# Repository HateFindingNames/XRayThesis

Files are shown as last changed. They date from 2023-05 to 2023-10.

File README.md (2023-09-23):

<!-- LTeX: language=en-EN -->

- [1. :construction: Main Document](#1-construction-main-document)
- [2. 🔩 Hardware At Hand](#2--hardware-at-hand)
  - [2.1. Source](#21-source)
    - [2.1.1. 📜 Documentation](#211--documentation)
  - [2.2. Detector](#22-detector)
    - [2.2.1. 📜 Documentation](#221--documentation)
- [3. 👀 Stuff to do](#3--stuff-to-do)
- [4. 💸 Shopping Lists](#4--shopping-lists)
  - [4.1. Hardware](#41-hardware)
  - [4.2. Fasteners](#42-fasteners)
- [5. Drafting Area](#5-drafting-area)

# 1. :construction: Main Document

Since there is no reasonable way to track updated PDFs in git I will place them on [my Onedrive :globe_with_meridians:](https://hsrheinmain-my.sharepoint.com/:b:/g/personal/lmy9f42u92_hsrheinmain_onmicrosoft_com/EdXuY1hF2GhHoTZ-xGF3LT8B4NocIp0KUSrm5S4OvCQvuw?e=4TwyDO) until it is somewhat ready to publish.

# 2. 🔩 Hardware At Hand

## 2.1. Source

**Magpro TUB00154-SA-W06:**

* XRF and X-ray imaging
* 60kV (70 keV?)
* Spot size (.25 x 1.07)mm
* Cone divergence 48°
* ~17.6e3cps @ 16.4uA (40kV)

**SA** => SPI (**S**) and Analog (**A**) control type

**W06** => Tungsten target (transmition lines provided by [NIST](https://physics.nist.gov/cgi-bin/XrayTrans/search.pl?element=W&lower=&upper=&units=eV))

Made by [Moxtek](https://moxtek.com/) and distributed (EU) by [Quantum Design](https://qd-europe.com/de/de/)

### 2.1.1. 📜 Documentation

Available documentation can be found inside this repo:

* [DATASHEET_TUB00154-SA-W06.pdf](docs/OnPaper/DATASHEET_TUB00154-SA-W06/DATASHEET_TUB00154-SA-W06.pdf)
* [MANUAL_TUB-MAN-1007.pdf](docs/OnPaper/MANUAL_TUB-MAN-1007/MANUAL_TUB-MAN-1007.pdf)
* [TUB-DATA-1013-MAGPRO.pdf](docs/Online/TUB-DATA-1013-MAGPRO.pdf)

and on my OneDrive:

* [🔒 Moxtek MagPro 70kV  XRF Source (TUB00154-XX-XXX  TUB00155-XX-XXX) Product Specification (TUB-SPEC-1033) Rev H.pdf](https://hsrheinmain-my.sharepoint.com/:b:/g/personal/lmy9f42u92_hsrheinmain_onmicrosoft_com/EV1KUsbPE4NGpiN00cES0QcBQOVuTafLMZQphgjChVBe-A?email=daniel.muenstermann%40hs-rm.de&e=YY6j7k)
* [🔒 TUB00154-XX-XXX Mechanical Drawing.pdf](https://hsrheinmain-my.sharepoint.com/:b:/g/personal/lmy9f42u92_hsrheinmain_onmicrosoft_com/Eb5gZbNKkz1OtNJbWsKaR_sB0skO_YVYC2-HvIApNUwNWA?email=daniel.muenstermann%40hs-rm.de&e=mrExvE)

## 2.2. Detector

SDD Detector made by *PN Detector*: [XRS-A (All-in-One)](https://pndetector.de/products-applications/the-xrf-spectrometer-all-in-one/)
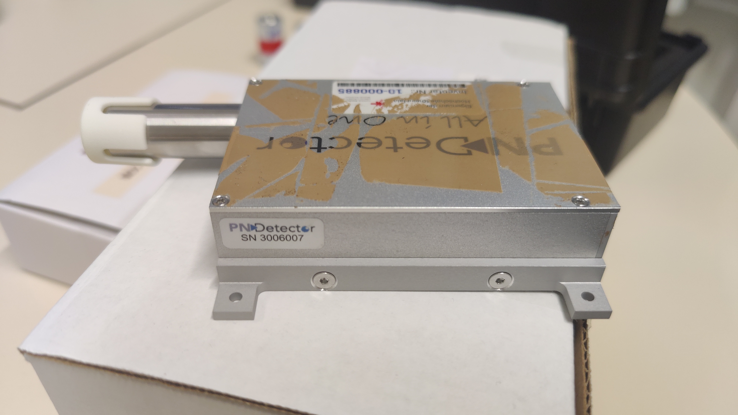
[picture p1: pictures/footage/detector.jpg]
SDD Detector


### 2.2.1. 📜 Documentation

OneDrive:

* [🔒 User Manual - XRS-A-30-128-200-MLC+GUI 0.1.1 -3006007.pdf](https://hsrheinmain-my.sharepoint.com/:b:/g/personal/lmy9f42u92_hsrheinmain_onmicrosoft_com/EWPr4Hw9F3tDvXxqMdxp95wBGIPgKuyxWKV6rSSlt5RyFA?email=daniel.muenstermann%40hs-rm.de&e=1WMr1p)

# 3. 👀 Stuff to do

In no particular order:

* [x] Text *[Quantum Design](https://qd-europe.com/de/de/)* about
  * [x] Linux-Software available?
  
    >*"No, only Microsoft"*

    * [ ] Make custom software?
  * [x] how to switch analog <=> digital control

    >*"10-pin is programmed for either I2C, SPI or Analog at the factory.  If a customer orders with Analog, they need to run digital through the USB or send back for reprograming and testing."*

  * [x] further documentation

    >*"FYI, 12W can operate down to -5kV setting, but the spec docs currently talk to the settings for 40kV and above.  If the customer wants to operate below 40kV, the voltage is scaled linearly from 0-4.667VDC for 0 to -70kV(but will not run at all at voltages less than -4kV setting), and 0-4VDC for 0 to 1000uA current setting.  Current needs to be limited to not exceed 12W total power, so 1,000uA does not work well above 12kV setting, and they will need to reduce the emission current as they select higher kV to keep power at or below 12W.  -W06 target is really not meant to be run below 40kV, as the W coating is thick enough that it blocks a majority of the flux intensity at kV settings below 30kV.  They can run down as low as 30kV, but stability may be affected in their application below 40kV setting."*

    Additional spec sheet and drawings are made available 👌 but are classified. => Plz check [OneDrive](https://hsrheinmain-my.sharepoint.com/:f:/g/personal/lmy9f42u92_hsrheinmain_onmicrosoft_com/Eu1u_OxAc6tNtfoioA8n_JEBt5x4kzV99mTDH0zqPgQLmQ?email=daniel.muenstermann%40hs-rm.de&e=uNh9up).
  * [x] CAD files => DIY
* [ ] Enclosure options
  * [ ] [Zarges-Boxes](https://www.zarges.com/de/produkte/verpacken-transportieren/kisten)?
  * [ ] [Rüger](https://www.rueger-industriebedarf.com/) (local distributer sells them among other, cheaper brands)
  * Interior modification:
    * [ ] Interlock
    * [ ] Pb-Shielding
      * [ ] Determine necessity
      * [ ] Find distributor => pre-order
* [ ] Make CAD-Model
* [x] Detector (check [*Amptek*](https://www.amptek.com/products/x-ray-detectors/x-ray-detector-selection-guide))
  * Options:
    * ~~**Si**licon **P**ositive **I**ntrinsic **N**egative Diode (Si-PIN Diode) (Wiki: [de](https://de.wikipedia.org/wiki/Pin-Diode),[en](https://en.wikipedia.org/wiki/PIN_diode))~~
    * 👉 **S**ilicone **D**rift **D**etector (SDD) (Wiki: [de](https://de.wikipedia.org/wiki/Siliziumdriftdetektor),[en](https://en.wikipedia.org/wiki/Silicon_drift_detector))
    * ~~**Ca**dmium **Te**lluride Schottky Diode (CdTe-Schottky)~~
* [ ] X-Ray optics

# 4. 💸 Shopping Lists

## 4.1. Hardware

| **Items**                                                                                                                                                                                                                                                              |        **Moneys** | **Vendors**           |    **Ordered**     |    **Arrived**     |
| ---------------------------------------------------------------------------------------------------------------------------------------------------------------------------------------------------------------------------------------------------------------------- | ----------------: | --------------------- | :----------------: | :----------------: |
| [Ball Bearing 635-2RS](https://www.kugellager-express.de/miniatur-kugellager-635-2rs-5x19x6-mm)                                                                                                                                                                        |        10 x 0.79€ | Kugellager-Express.de | :heavy_check_mark: | :heavy_check_mark: |
| [Ball Bearing 61708](https://www.kugellager-express.de/rillenkugellager-6708-61708-2rs-40x50x6-mm)                                                                                                                                                                     |         2 x 8.20€ | Kugellager-Express.de | :heavy_check_mark: | :heavy_check_mark: |
| [PRT-01-60](https://www.igus.de/product/iglidur_PRT_01_AL_J?artnr=PRT-01-60) (Slewing Bearing)                                                                                                                                                                         |           174.78€ | Igus.de               | :heavy_check_mark: | :heavy_check_mark: |
| Drag Chain                                                                                                                                                                                                                                                             | For free :muscle: | Igus.de               | :heavy_check_mark: | :heavy_check_mark: |
| ~~[Pulley 60T](https://www.amazon.de/Saipor-Zahnriemenrad-Riemenscheibe-Synchronrad-Zahnriemenscheibe/dp/B08ZSL7BH9/ref=sr_1_2?keywords=pulley%2B60t&sr=8-2&th=1)~~ printed                                                                                            |         ~~9.79€~~ | ~~Amazon.de~~         |        :x:         |                    |
| ~~[Pulley 20T](https://www.kris3d.de/products/pulley-20t-2gt-w9-b5-black)~~                                                                                                                                                                                            |     ~~2 x 3.99€~~ | ~~kris3d.de~~         |        :x:         |                    |
| [Belt 342-2MGT3-6](https://www.keilriemenexpress.de/zahnflachriemen-zahnriemen-shop/gates-zahnriemen-powergrip-gt3/zahnflachriemen-2m-gt3/zahnflachriemen-2m-gt3-6-mm/2mgt3-342-lw-6-mm-powergripr-gt3.html) (Sample)                                                  |            12.10€ | KeilriemenExpress.de  | :heavy_check_mark: |   :heavy_check_mark:                 |
| [Belt 600-2MGT3-9](https://www.keilriemenexpress.de/zahnflachriemen-zahnriemen-shop/gates-zahnriemen-powergrip-gt3/zahnflachriemen-2m-gt3/zahnflachriemen-2m-gt3-9-mm/2mgt3-600-lw-9-mm-powergripr-gt3.html) (Detector)                                                |            16.55€ | KeilriemenExpress.de  | :heavy_check_mark: | :heavy_check_mark: |
| [Filament eSun ASA 1kg](https://www.3djake.de/esun/easa-schwarz)                                                                                                                                                                                                       |        2 x 26.99€ | 3DJake.de             | :heavy_check_mark: | :heavy_check_mark: |
| ~~[Stepper Motors](https://www.amazon.de/STEPPERONLINE-Schrittmotor-55Ncm-Meter-3D-Drucker/dp/B0B93HTR87/ref=sr_1_6?__mk_de_DE=%C3%85M%C3%85%C5%BD%C3%95%C3%91&crid=2FD8SIDGO2PCX&keywords=stepperonline&sprefix=stepperonline%2Caps%2C98&sr=8-6&th=1)~~ self supplied |    ~~2 x 10.99€~~ | ~~Amazon.de~~         |        :x:         |                    |
| ~~[PSU 5V](https://www.digikey.de/en/products/detail/mean-well-usa-inc/RS-25-5/7706180)~~                                                                                                                                                                              |        ~~14.23€~~ | ~~Digikey.de~~        | :heavy_check_mark: | :heavy_check_mark:                   |
| ~~[PSU 24V](https://www.digikey.de/en/products/detail/mean-well-usa-inc/LRS-150-24/7705015)~~                                                                                                                                                                          |        ~~26.54€~~ | ~~Digikey.de~~        | :heavy_check_mark: | :heavy_check_mark:                   |
| [Aluminum Box](https://www.aluboxen-shop.de/aluboxen-mit-deckel/alukiste-xxl-130-liter)                                                                                                                                                                                |            99.90€ | aluboxen-shop.de      | :heavy_check_mark: |   :heavy_check_mark:                 |
| [Aluminum EN AW 5083 (8x505x770)mm](https://www.gemmel-metalle.de/aluminium/platten/5083/aluminiumplatte-213.html)                                                                                                                                                     |            96.70€ | gemmel-metalle.de     | :heavy_check_mark: |  :heavy_check_mark:                  |
| [Lead Sheet (1x300x5000)mm](https://sanundo.de/sonstiges/dach-zubehoer/walzblei/56046/selbstklebendes-farbiges-walzblei-bleicolor-sk-300mm-rotbraun-aehnlich-ral-8012-meterware)                                                                                       |            112.5€ | sanundo.de            |                    |                    |
| ~~Shipping (Alu, Lead)~~                                                                                                                                                                                                                                               |        ~~99.50€~~ | gemmel-metalle.de     |                    |                    |
| [Stepper Driver](https://www.digikey.de/de/products/detail/trinamic-motion-control-gmbh/TMC2209SILENTSTEPSTICK/10232488)                                                                                                                                               |        2 x 18.22€ | digikey.de            |                    |                    |
| ~~[DAC](https://www.digikey.de/de/products/detail/microchip-technology/MCP4912-E-P/2332828)~~ Self sourced    |             ~~2.86€~~ | digikey.de            |    :heavy_check_mark:                |      :heavy_check_mark:              |
| [ADC](https://de.rs-online.com/web/p/ad-wandler/0403115?gb=s)    |        2 x 4.68€ | rs-online.com.de            |     :heavy_check_mark:               |      :heavy_check_mark:              |
| [5V Reference](https://de.rs-online.com/web/p/referenzspannungs-ics/5343065?gb=s)    |        0.83€ | rs-online.com.de            |       :heavy_check_mark:             |       :heavy_check_mark:             |
| [2.5V Reference](https://de.rs-online.com/web/p/referenzspannungs-ics/5343059?gb=s)    |        0.92€ | rs-online.com.de            |          :heavy_check_mark:          |     :heavy_check_mark:               |
| ~~**Total**~~          |   ~~**637.73€**~~ |                       |        :x:         |                    |
| **Total**              |       **718.25€** |                       |        :x:         |                    |

## 4.2. Fasteners

| **Items**                                                                                                | **Moneys** | **Vendor**        |    **Ordered**     |    **Arrived**     |
| -------------------------------------------------------------------------------------------------------- | ---------: | ----------------- | :----------------: | :----------------: |
| [M5x25 DIN912](https://www.schraubenluchs.de/100-Stueck-Zylinderschrauben-ISO-4762-DIN-912-A2-70-M-5x25) |      5.75€ | schraubenluchs.de | :heavy_check_mark: | :heavy_check_mark: |
| [M5x50 DIN912](https://www.schraubenluchs.de/100-Stueck-Zylinderschrauben-ISO-4762-DIN-912-A2-70-M-5x50) |     14.65€ | schraubenluchs.de | :heavy_check_mark: | :heavy_check_mark: |
| [M5x20 DIN912](https://www.schraubenluchs.de/100-Stueck-Zylinderschrauben-ISO-4762-DIN-912-A2-70-M-5x20) |      4.82€ | schraubenluchs.de | :heavy_check_mark: | :heavy_check_mark: |
| [M5 Hex Nut](https://www.schraubenluchs.de/200-Stueck-Sechskantmuttern-DIN-934-A2-M5)                    |      2.50€ | schraubenluchs.de | :heavy_check_mark: | :heavy_check_mark: |
| **Total**                                                                                                | **27.72€** |                   |                    |                    |

# 5. Drafting Area

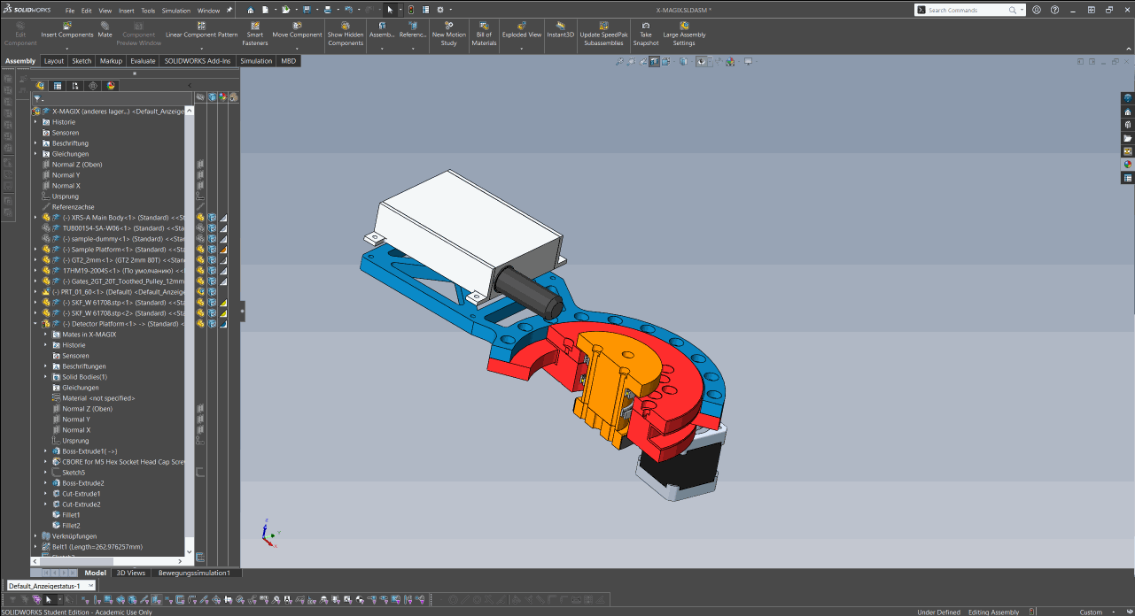
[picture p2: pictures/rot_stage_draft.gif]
Rotary stage WIP

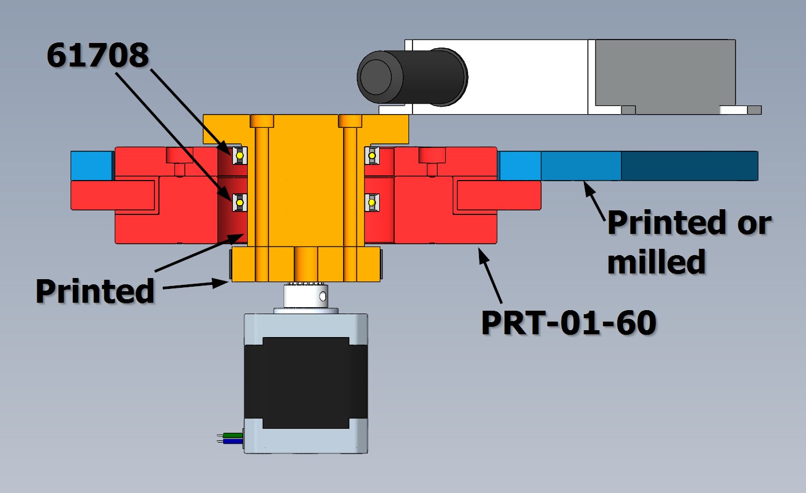
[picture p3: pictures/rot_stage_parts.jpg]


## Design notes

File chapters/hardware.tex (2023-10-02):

\chapter{Hardware}\label{chap:hardware}
    The hardware side consists of two mechanically connected but kinematically independent goniometer stages, static mounting components and an electrical part.
    The electronics are subdivided into the power supply, motion and logic handling and an interface between XRS/detector/motion system and the logic.

    \section{Mechanics}\label{sec:mechanics}
        Mechanically, the main challenge is to build two co-axial and co-planar but kinematically independent operating goniometer stages;
        One to move the detector and one to move the specimen about their mutual center of rotation as shown in~\cref{fig:rough sketch of the motion system}.
        \begin{figure}[!h]
            \centering
            \includesvg[width=.4\textwidth]{drawings/sketch_stages}%
            \caption[Rough sketch of the motion system]{Rough sketch of the motion system.}%
            \label{fig:rough sketch of the motion system}%
        \end{figure}
        Let the light bulb depicted in~\cref{fig:rough sketch of the motion system} be an x-ray source.
        The eye represents the detector and the specimen to analyze is positioned in the center\footnote{Clearly, an X-Ray source most likely will not be found in the fashion of an actual incandescent light bulb. Here, it merely serves as a visual shortcut representing a photon source. Furthermore, an actual eye performs rather poor at detecting \(\gamma\)-radiation. Thus, it, as well, shall serve the purpose of representation.}.
        The central stage carrying the sample varies the angle~\(\theta\), which is the angle enclosed by the incident beam path and the plane of the specimen.
        The detector stage~--~the outer circle in~\cref{fig:rough sketch of the motion system}~--~gets positioned along an angle~\(\varphi\).\par\medskip

        Since x-ray diffraction spectroscopy relies on angle-dependent intensity measurements both stages need to be capable of accurate and repeatable positioning at best possible angular resolution.
        Additionally, the detector stage needs to accelerate and carry the mass of the actual detector and its supporting structure.

        The rise of desktop 3D-printing and the growing communities around highly sophisticated open source/hardware machines has made components for high precision yet low cost motion systems in the low to lower-mid power range more available than ever.
        To this end, common 3D-printer parts are used where applicable.
        To achieve accuracy, a gearing system utilizing stepper motors, purpose-made timing pulleys and timing belts with a GT3 profile and~\qty{2}{\milli\metre} pitch are chosen~\cite{Manual.POWERGRIPGT3,Manual.LIGHTPOWERPRECISION}.
        
        To achieve and maintain repeatability~--~besides other factors~--~springiness in the motion system needs to be reduced to a minimum and slip during changes of torque e.g. direction changes and/or acceleration and deceleration needs to be eliminated.
        The former can reasonably easy be achieved by choosing fiberglass lined timing belts and proper preloading of the drive system removes residual slip.\par\medskip

        % A detailed description of the in this work proposed solutions are discussed in~\cref{sec:sample stage,,sec:detector stage}.
        
        \subsection{Sample Stage}\label{sec:sample stage}
            \Cref{fig:xmagix full sample highlightes} shows the main kinematic assembly and the sample stage with drive highlighted in light blue.
            \begin{figure}[!ht]
                \centering
                \includesvg[width=.7\textwidth]{drawings/X-MAGIX_full_sample}%
                \caption[Full motion system. Sample stage highlighted in light blue]{Full motion system. Sample stage highlighted in light blue.}%
                \label{fig:xmagix full sample highlightes}%
            \end{figure}%

            The center part of the main assembly is the slewing ring \textit{PRT-01-60} by \textsc{igus}~\cite{Manual.IglidePRTPolymerSlewingRings.} depicted as no. 24 in the section view in~\cref{fig:sample stage exploded section}.
            Its relatively large central hole gives room to place a smaller bearing assembly so that its is coaxial to its own axis of rotation.\par\medskip

            \begin{figure}[!h]
                \centering
                \includesvg[width=.3\textwidth]{pictures/footage/stage_bearings}
                \caption[Detailed photo of the stator center]{Detailed photo of the stator center. Close-up view of the press-in-place stator center locks (1). At the top and bottom are the \textit{W 61708} bearings visible (2) with the \textit{stator center spacer} in between (4). The outer part is the \textit{stator center} itself (3). All parts except the bearings are 3D-printed in acrylonitrile butadiene styrene (ABS).}%
                \label{fig:detailed view of the stator center}
            \end{figure}
            \nomenclature[A]{ABS}{Acrylonitrile butadiene styrene}

            The stationary part of the slewing ring provides two circular patterns of tapped bores fitting 10 M5 fasteners each.
            The holes along the inner circle are free to use.
            \textit{Stator center} (no.~4) is inserted into the slewing ring and held in place by seven \textit{M5x10} bolts (no.~22).
            Hereafter and in that sequence, the \textit{stator center spacer} (no.~5) and ball bearing \textit{W 61708-2RS} gets inserted into the free space from the top.
            The ball bearing is secured by press-fitting six of the \textit{stator locks} into their respective slots\footnote{ ``Abusing'' an ordinary drill-press to~--~well~--~press them in place (turned off!) works perfect.}.
            The final sub-assembly is shown in~\cref{fig:detailed view of the stator center}.

            With slight force, the remaining bearing is slid in its appropriate position from the bottom against the \textit{stator center spacer} as well.
            Finally, the \textit{sample driven gear} (no.~2) and the \textit{endstop bump sample} (no.~17) are tightened together against the \textit{sample platform} (no.~1) which is placed into the bearings beforehand.
            In order to guide the timing belt later, two bearings stacks are screwed from the bottom into two adjacent tapped holes.\par\medskip

            Not shown in~\cref{fig:sample stage exploded section} is the driving sub-assembly for the sample stage.
            Since its assembly is considered straightforward and a more complex version is shown in~\cref{fig:detector drive exploded}, an assembled view is found in~\cref{fig:sample drive} for reference.

            \begin{figure}[!h]
                \centering
                \includesvg[width=.8\textwidth]{drawings/sample_stage_-_exploded_section}%
                \caption[Sample stage exploded view~-~sectioned]{Sample stage exploded view~-~sectioned. 1: Sample Platform, 2: Sample Driven Gear 80T, 3: W 61708, 4: Stator Center, 5: Stator Center Spacer, 9: M5 Hex nut, 10: M5x25, 13: Washer 5.3, 16: 635-2RS, 17: Endstop Bump Sample, 19: M5x55, 20: M5x50, 21: Stator Center Spacer Lock, 22: M5x10, 24: PRT-01-60.}%
                \label{fig:sample stage exploded section}%
            \end{figure}

        \subsection{Detector Stage}\label{sec:detector stage}
            The components comprising the detector stage are depicted in~\cref{fig:xmagix full detector highlightes}.
            Its principle of operation follows the same basic concept~--~a timing belt mechanically couples the driving sub-assembly on the right-hand side to the movable central platform.\par\medskip

            \begin{figure}[!ht]
                \centering
                \includesvg[width=.7\textwidth]{drawings/X-MAGIX_full_detector}%
                \caption[Full motion system. Detector stage blue highlighted]{Full motion system. Detector stage blue highlighted.}%
                \label{fig:xmagix full detector highlightes}%
            \end{figure}

            Again, the detector stage is subdivided into a driving sub-assembly as shown in~\cref{fig:detector drive exploded} and driven one shown in~\cref{fig:detector stage exploded} respectively.
            The driven portion of the detector stage only consists of two main parts mounted to the slewing ring;
            The \textit{detector platform} (no.~25) which is placed on the top at an arbitrary orientation and the \textit{detector driven gear} (no.~26) on the bottom of the slewing ring.
            \textit{M5x25} (no.~10) bolts and \textit{hex nuts} (9) are placed into all holes but the two where the \textit{endstop bump detector} (no.~29) is mounted.
            To accommodate the needed extra length here, \textit{M5x30} (no.~42) bolts are used instead.
            The \textit{endstop bump detector} itself is oriented such that its outermost mounting hole is aligned with the hole at the clockwise end of the detector arm.
            To lift the detector to a suitable height above the \textit{sample platform}, \textit{detector spacers} (no.~30) are placed underneath the \textit{XRS-A} (no.~23).\par\medskip

            \Cref{fig:detector drive exploded} shows an exploded view of the detector drive sub-assembly.
            The core component, a NEMA17 \num{200} steps per revolution stepper motor (no.~7), is placed on the inside of the housing (no.~27) and held in place by four \textit{M3x6} screws.
            Slotted screw holes allow easier installation of the timing belt and adjustment of tension later on.
            Together with a \textit{hex nut} and the \textit{belt tensioner} (no.~8), a \textit{M5x25} bolt allows to hold the motor in place while tensioning the belt prior to finally tightening the screws at the top.

            \begin{figure}[!h]
                \centering
                \includesvg[width=.8\textwidth]{drawings/detector_stage_-_exploded}%
                \caption[Detector stage -- exploded view]{Detector stage -- exploded view. 9: M5 Hex Nut, 10: M5x25, 23: XRS-A, 25: Detector Platform, 26: Detector Driven Gear 250T, 29: Endstop Bump Detector, 30: Detector Spacer, 31: M3x25, 42: M5x30.}%
                \label{fig:detector stage exploded}%
            \end{figure}
            
            Bearing stacks identical to those seen in~\cref{fig:sample stage exploded} are put in place to confine the belt path along a \qty{180}{\degree} loop around the \textit{80T} timing pulley (no.~28).
            Having as many teeth of the belt engage the pulley at any given time is preferred as it ensures good torque transmission without belt slipping at a lower overall belt tension and thus lower load on the motors.
            \begin{figure}[!h]
                \centering
                \includesvg[height=.4\textheight]{drawings/detector_drive_-_exploded}
                \caption[Detector stage drive~--~exploded view]{Detector stage drive~-~exploded view. 7: 17HM19-2004S, 8: Belt Tightener, 9: M5 Hex nut, 10, M5x25, 11: Washer 3.2, 12: M3x6, 13: Washer 5.3, 14: Motor Mount Socket, 16: 635-2RS, 27: Motor Mount Detector Drive, 28: GT3 \qty{2}{\milli\meter} 80T.}
                \label{fig:detector drive exploded}
            \end{figure}

        \subsection{Base and X-Ray Source}
            \begin{figure}[!ht]
                \centering
                \includesvg[width=.6\textwidth]{drawings/source_exploded}
                \caption[short]{title}%
                \label{fig:source exploded}
            \end{figure}

    \clearpage
    \section{Electronics}\label{sec:electronics}
        On the electronics side, several tasks need to be accomplished, the most basic of which is powering each of the system's components.
        The SBC is typically powered via its dedicated USB-C port, which in turn requires a \qty{5.1}{\volt} supply with a recommended current rating of \qty{3}{\ampere}~\cite{Manual.Documentation.RPF}.
        The detector's specifications state that it needs a \qty{5}{\volt} power supply and draws less than \qty{3}{\watt}, which translates to \(<\qty{0.6}{\ampere}\).
        Taken from the datasheet, the XRS is driven by an input voltage of \qty{24}{\volt} and an input current of \qty{1.1}{\ampere}~\cite{Manual.MAGPRODataSheet.QD}.
        The two stepper motors are each driven by \textit{TMC2209} stepper drivers which in turn accept a relatively broad range of \qtyrange{4.75}{29}{\volt}~\cite{Manual.TMC2209Datasheet} as supply voltages.
        The remaining peripherals such as the interface between the SBC and the XRS are directly driven from \qty{3.3}{\volt} and \qty{5}{\volt} provided by the Raspberry Pi's GPIO-Header.

        A tabulated summery of the supply power requirements can be found in~\cref{tab:power requirements}.\par\medskip
        \begin{table}[!h]
            \centering
            \caption[Electrical power requirements of the various installed components]{Electrical power requirements of the various installed components.}%
            \label{tab:power requirements}
            \begin{tabular}{@{}lSS@{}}
                \toprule
                Component&  {Voltage / \unit{\volt}}&    {Current / \unit{\ampere}}\\
                \midrule
                SBC&            5.1&    3.0\\
                Detector&       5.0&    0.6\\
                XRS&            24.0&   1.1\\
                Motor Driver&   24.0&   3.0\\
                \bottomrule
            \end{tabular}
        \end{table}

        Following the considerations above, a \qty{5}{\volt} \qty{25}{\watt} power supply unit (PSU) \nomenclature[A]{PSU}{Power Supply Unit} (\textit{RS-25-5}) and a \qty{24}{\volt} \qty{150}{\watt} PSU (\textit{LRS-150-24}) are installed.
        Each is able to deliver slightly more power than expected to be necessary, thus, leaving headroom for future extensibility and peaks in power demand.
        The single \qty{24}{\volt}-PSU supplying the stepper drivers and the XRS minimizes complexity and reduces costs.\par\medskip

        All wiring~--~where applicable~--~is routed through perforated cable ducting.

        \subsection{Kinematics}\label{sec:kinematics}
            In addition to the two stepper motors driving each stage, at least one endstop needs to be installed per axis.
            Despite inferior durability compared to optical or magnetic options, mechanical micro switch type endstops were chosen due to availability and simplicity by requiring no additional passive components.
            \begin{figure}[h]
                \centering
                
                \caption[Wiring of the used mechanical endstops]{Wiring of the used mechanical endstops. They are installed in normal closed (NC) configuration to detect faulty connections early on.}%
                \label{fig:endstop pic}
            \end{figure}

            \Cref{fig:endstop pic} shows an example of one of the actual endstops used.
            They are wired in normally closed (NC) configuration to prevent potential damage by driving the stages past their minimal position during the homing procedures in case of an accidental connection break.

            \begin{figure}[h]
                \centering
                \includesvg[width=.9\textwidth]{electronics/pdf/octopus}
                \caption[Top view drawing of the \textit{Octopus v1.0} PCB layout]{Top view drawing of the \textit{Octopus v1.0} PCB layout~\cite{Manual.BigTreeTechOctopus}. Highlighted are the power terminals (1), the used motor (2) and endstop (3) connectors and the USB type C plug (4). The motors and the main power supply share the same \qty{24}{\volt} supply and are tied together.}%
                \label{fig:octopus connections}
            \end{figure}

            Low-level processing of the endstop signaling and stepping pulse generation takes place on dedicated peripheral hardware connected to the SBC via USB.
            Usually found in 3D-printing appliances, an \textit{Octopus v1.0} is installed to accept motion instructions from and return endstop signals to the host system.
            \Cref{fig:octopus connections} depicts a top view diagram of the \textit{Octopus'} PCB\footnote{Printed Circuit Board\nomenclature[A]{PCB}{Printed Circuit Board}} layout and highlights the relevant connectors and terminals~\cite{Manual.BigTreeTechOctopus}.
            The power supply terminals located on the left hand side serve as power supply to the connected motor drivers, the board itself and an~--~if installed~--~heated print bed.
            In this design, the motors and the primary power supply of the board share the same voltage level of \qty{24}{\volt} (1).
            The two motors are connected to the first two 4-pin connectors at the top of horizontal row labeled \texttt{MOTOR0} and \texttt{MOTOR1}(2).
            There are four dedicated endstop connectors (3) located on the bottom right, each providing a ground connection and \qty{3.3}{\volt}\footnote{Depending on the respective jumper placement \qty{5}{\volt} can be chosen as well. See~\cite{Manual.BigTreeTechOctopus} for the exact jumper location.}.

            \begin{table}[h]
                \centering
                \caption[\textit{Octopus} pin assignment]{\textit{Octopus} pin assignment.}
                \label{tab:octopus pin assignments}
                \begin{tabular}{@{}lrr@{}}
                    \toprule
                    Function&   X-axis pin& Y-axis pin\\
                    \midrule
                    Step&       PF13&   PG0\\
                    Direction&  PF12&   PG1\\
                    Enable&     !PF14&  !PF15\\
                    Endstop&    \textasciicircum PG6&   \textasciicircum PG9\\
                    Driver UART& PC4&   PD11\\
                    \bottomrule
                \end{tabular}
            \end{table}

            The endstop switches are connected between ground and the input pin with the internal pull-up resistor enabled.
            The host system is connected to the board via USB type C to be found on the right-most edge of the board (4).
            The logic level rails of the \textit{Octopus} could be powered by the USB \qty{5}{\volt}-bus power by placing the respective jumper accordingly.
            Doing so is neither required, nor is it advisable, as this would put unnecessary additional load on the SBC's \qty{5}{\volt} supply.
            The default jumper configuration lets an on-board voltage regulator handle conversion from the input voltage range down to \qty{5}{\volt} and \qty{3.3}{\volt}.

            A dedicated stepper driver of type \textit{TMC2209} placed beneath the respective connector for each motor.
            The \textit{TMC2209} features various modes of operation each of which can be manipulated dynamically during operation.
            The \textit{Octopus'} microcontroller (MCU)\nomenclature[A]{MCU}{MicroController Unit} communicates with the drivers via 1-wire UART\nomenclature[A]{UART}{Universal Asynchronous Receiver-Transmitter}, needing a special pin assignment for each driver.\par\medskip

            The final pin assignments are summarized in \cref{tab:octopus pin assignments}.

        \subsection{Raspberry Pi to X-Ray Source Interface}\label{sec:xrs interface board}
            The most straightforward way of operating and monitoring the XRS would be connecting to its dedicated USB-B port and using their GUI tool ``12WattController''.
            It allows to set and monitor the tube's acceleration voltage as well as the filament current, monitoring the devices on/off state, parametrizing and activating PWM operation mode and setting up an auto-shutdown timer.
            Unfortunately, the software only runs under \textsc{Microsoft} Windows and there are no means of accessing the control schemes programmatically.

            \begin{table}[!h]
                \centering
                \caption[Pinout of the analog control connector of the XRS]{Pinout of the analog control connector of the XRS. Transcribed from the included users manual.}%
                \label{tab:xrs 10pin connector specs}
                \begin{tabular}{@{}llll@{}}
                    \toprule
                    Pin&    Function&      I/O Value&                                                          Response/Description\\
                    \midrule
                    1&      HV Enable&      \qtyrange{0.0}{+5.0}{\volt} (Input \(Z = \qty{10}{\kilo\ohm}\))&     \(< \qty{1.0}{\volt} = \text{OFF, } >\qty{4}{\volt} = \text{ON}\)\\
                    2&      Filament Ready& \qtyrange{0.0}{+5.0}{\volt} (Output \(Z = \qty{1}{\kilo\ohm}\))&     \(< \qty{1.0}{\volt} = \text{Not ready, } \qty{5}{\volt} = \text{Ready}\)\\
                    3&      HV Control&     \qtyrange{0.27}{+4.0}{\volt} (Input \(Z = \qty{100}{\kilo\ohm}\))&   \qtyrange{4}{60}{\keV}\\
                    4&      HV Monitor&      \qtyrange{0.27}{+4.0}{\volt} (Output \(Z = \qty{100}{\ohm}\))&       \qtyrange{4}{60}{\keV}\\
                    5&      Current Control& \qtyrange{0.04}{+4.0}{\volt} (Input \(Z = \qty{100}{\kilo\ohm}\))&   \qtyrange{10}{1000}{\uA}\\
                    6&      Current Monitor& \qtyrange{0.0}{+4.0}{\volt} (Output \(Z = \qty{100}{\ohm}\))&        \qtyrange{0}{1000}{\uA}\\
                    7&      Ground&         Ground&                                                             Ground\\
                    8&      Ground&         Ground&                                                             Ground\\
                    9&      Filament Enable&\qtyrange{0.0}{+5.0}{\volt} (Input \(Z = \qty{10}{\kilo\ohm}\))&     \(< \qty{1.0}{\volt} = \text{OFF, } >\qty{4}{\volt} = \text{ON}\)\\
                    10&     Input Power&    \(\qty{24}{\volt} \pm \qty{5}{\percent}\)&  Input Power\\
                    \bottomrule
                \end{tabular}
            \end{table}

            Located next to the USB-B port is a 2x5 pin connector allowing analog control of the device and monitoring of its state%
            \footnote{%
            Mfr. No. \textit{IPL1-105-01-L-D-RA-K} according to the XRS manual.%
            }.
            \Cref{tab:xrs 10pin connector specs} is taken directly from the technical user guide included with the XRS:%
            \footnote{%
            Unfortunately, neither the manufacturer \textsc{Moxtek}, nor the reseller \textsc{Quantum Design Europe} provide freely accessible resources besides the cited data sheets~\cites{Manual.MAGPRODataSheet.MOXTEK}{Manual.MAGPRODataSheet.QD}.
            Therefore, this work will only provide contextually necessary transcripts of relevant parts of the included documents.}
            Pins 1, 3, 5 and 9 are inputs, of which pins 1 and 9 are digital controls.
            Current Control and HV Control\nomenclature[A]{HV}{High Voltage} are set by manipulating the voltage levels on pins 3 and 5.
            The SBC only provides pseudo-analogous control via built-in hardware pulse width modulation (PWM)\nomenclature[A]{PWM}{Pulse Width Modulation} \textquote{available on GPIO12, GPIO13, GPIO18, GPIO19}~\cite{Manual.Documentation.RPF}.
            PWM-control works by switching between logic-Hi and logic-Lo at a set frequency while varying the ratio between the times the signal is in Hi-state and Lo-state during one period.
            While this is acceptable with sufficiently slow reacting systems i.e. systems exhibiting low-pass behavior such as speed-control of brushed DC-Motors or brightness control of an LED taking advantage of the refresh rate of the human visual system, achieving a stable and reliable control of the XRS by means of PWM is highly unlikely.
            Instead, a true analog signal is generated and fed to the \textit{XRS}' inputs.

            \begin{figure}[h]
                \centering
                \includesvg[width=.6\textwidth]{electronics/pdf/DAC_circuitry}
                \caption[Schematic of the DAC]{Schematic of the DAC.}%
                \label{fig:DAC schematic}
            \end{figure}

            Due to time restrictions, a rather crude interface board was made, utilizing a two-channel digital-to-analog converter (DAC) for writing to the XRS and a two-channel analog-to-digital converter (ADC) for reading it.
            To generate analog signals, the component \textit{TLV5618A} was used.
            It integrates two separate output channels with \(n = \qty{12}{\bit}\) resolution, delivers peak output voltages ranging from \qtyrange{2.7}{5.5}{\volt} and is SPI\nomenclature[A]{SPI}{Serial Peripheral Interface} programmable~\cite{Manual.DAC.TLV5618A}.
            The schematic depicted in~\cref{fig:DAC schematic} shows its external circuitry and the configuration of its voltage reference.
            In order to prevent clipping of the output voltage, it is important to keep the reference voltage below \(\frac{V_{DD} - \qty{0.4}{\volt}}{2}\) which effectively means keeping it below half the maximum desired output voltage~\cite[p. 3]{Manual.DAC.TLV5618A}.
            The utilized \textit{LT1009} delivers a sufficiently stable reference voltage of \(\approx \qty{2.385}{\volt}\) with pin 3 tied to ground (see~\cref{fig:LT1009 sim} for spice simulation analysis).
            % Although this still is slightly higher than the limits stated above, minimal clipping of the output voltage should not be of a concern.

            \begin{equation}
                2REF\frac{CODE}{2^n} = FS \qquad \text{where} \qquad CODE \overset{!}{=} 2^n
                \label{eq:dac general function}
            \end{equation}
            \nomenclature[L]{\(REF\)}{Reference Voltage\nomunit{\volt}}%
            \nomenclature[L]{\(n\)}{ADC/DAC bit resolution\nomunit{1}}%
            \nomenclature[L]{\(FS\)}{Full Scale range\nomunit{\volt}}%
            \begin{align}
                UNOB = \cint*{ U \cdot \frac{n - 1}{FS}}
                \label{eq:UNOB}
            \end{align}

            \Cref{eq:dac general function}, taken from the DAC's datasheet, specifies a full scale range (\(FS\)) of two times the reference voltage while the output voltage remains capped at \(V_{DD}- \qty{0.4}{\volt}\).
            The difference of \qty{0.17}{\volt} is expected to be clipped off of the full scale output signal.\par\medskip

            Taken from~\cref{tab:xrs 10pin connector specs} HV Control and Current Control are ranging from \(U_{DAC,A} = \qtyrange{0.27}{4}{\volt}\) and \(U_{DAC,B} = \qtyrange{0.04}{4}{\volt}\).
            These control ranges introduce upper and lower dead regions, rendering a number of bits in those regions unusable (\(UNOB\), see~\cref{eq:UNOB}).
            \Cref{fig:transfer function DAC} illustrates those dead regions.

            \begin{figure}[h]
                \centering
                \includesvg[width=\textwidth]{software/pictures/dac_transfer_function}
                \caption[Transfer function of the DAC showing the operational range]{Transfer function of the DAC showing the operational range.}%
                \label{fig:transfer function DAC}
            \end{figure}

            The expected minor clipping of the signal at the DAC's outputs is considered negligible since it will be well inside the upper (mutual) dead region.

            \begin{equation}
                R_S = \frac{U_S - U_Z}{I_Z + I_L}
                \label{eq:LM4040 cathode current}
            \end{equation}
            \nomenclature[L]{\(R_S\)}{Voltage references current limiting resistor\nomunit{\ohm}}%
            \nomenclature[L]{\(U_S\)}{Supply Voltage\nomunit{\volt}}%
            \nomenclature[L]{\(U_Z\)}{Voltage across the reference voltage diode\unit{\volt}}%
            \nomenclature[L]{\(I_Z\)}{Current through reference voltage diode\nomunit{\ampere}}%
            \nomenclature[L]{\(I_L\)}{Load current\nomunit{\ampere}}%

            The analogous feedback signal from the XRS is sampled by an \textit{MCP3202}~\cite{Manual.ADC.MCP3202}.
            The \textit{MCP3202} is a \qty{12}{\bit} two-channel ADC with an input range of \qtyrange{2.7}{5.5}{\volt} and SPI-programmable as well.
            It uses its power supply as its voltage reference, thus, the \textit{LT1009} needs to be replaced in favor of a \qty{5}{\volt} reference.
            As shown in~\cref{fig:ADC schematic}, a reference of type \textit{LM4040DIZ-5.0} is used.
            To provide a reference of \(\qty{5}{\volt} \pm \qty{2}{\percent}\), a cathode current of \qtyrange{0}{25}{\milli\ampere} must not be exceeded~\cite{Manual.LM4040PrecisionMicropowerShuntVoltageReference}.

            \begin{figure}[h]
                \centering
                \includesvg[width=.65\textwidth]{electronics/pdf/ADC_circuitry}
                \caption[Schematic of the ADC]{Schematic of the ADC.}%
                \label{fig:ADC schematic}
            \end{figure}

            With an assumed supply voltage \(U_S\) slightly higher than the nominal \qty{5}{\volt}, maximum expected load current of \(I_L = \qty{550}{\uA}\)\footnote{Operating current of the \textit{MCP3202}.} and a chosen diode current of \(I_Z = \qty{15}{\milli\ampere}\)~\cref{eq:LM4040 cathode current} yields a current limiting resistor of \(R_S \approx \qty{6}{\ohm}\)~\cite{Manual.LM4040PrecisionMicropowerShuntVoltageReference}.
            This value is readily achievable using two widely available E12 series resistors in parallel and is reflected in the two resistors \(R_4\) and \(R_5\) of \qty{12}{\ohm} each.\par\medskip

            The \textit{MCP3202} does not exhibit any clipping, letting the reference voltage be assumed equal the full scale voltage.
            The HV Monitor's output signal has the same upper and lower boundaries as the HV Control signal thus decreasing resolution and increasing the dead region compared to the DAC's performance.
            Again, in this application this is not considered problematic, since there is no need for sub-\unit{\kev} and sub-\unit{\uA} adjustability.

            \Cref{tab:adc dac performance summery} summarizes the theoretical performance data of the D/A and A/D converter circuits.
            \begin{table}[t]
                \centering
                \caption[Performance data of D/A and A/D circuitry]{Performance data of D/A and A/D circuitry.}%
                \label{tab:adc dac performance summery}
                \begin{tabular}{@{}lSSSS@{}}
                    \toprule
                    Value&          {HV Control}&   {Current Control}&  {HV Monitor}&   {Current Monitor}\\
                    \midrule
                    \(UNOB_L\)&     232&            35&                 222&            0{\tablefootnote{Since the filament current can not be practically set below \qty{10}{\uA} the effective \(UNOB_L\) is the same as that of current control.}}\\
                    \(UNOB_H\)&     662&            662&                819&            819\\
                    \(UNOB_{tot}\)& 894&            697&                1041&           819\\
                    Resolution&     \qty{0.017}{\kV\per\bit}& \qty{0.291}{\uA\per\bit}& \qty{0.018}{\kV\per\bit}& \qty{0.302}{\uA\per\bit}\\
                    \bottomrule
                    
                \end{tabular}
            \end{table}

            % The resolution in terms of \unit{\keV\per\bit} and \unit{\uA\per\bit}

            \Cref{fig:top view interface board} shows the top view of the real-world implementation of the above.
            The yellow area~(1) comprises the DAC portion of the circuit, the purple area~(2) the ADC.
            The 10-pin headers on the left and right connect to the SBC and the XRS.
            A detailed description of their respective pin-assignment can be found in the full schematics in~\cref{fig:schematics of peripherals}.
            The 2-pin connector on the upper right receives~\qty{24}{\volt} to supply the XRS via pin 10 on its connector.

            The pin ordering scheme for the 10-pin connector on the rear of the XRS is shown in~\cref{fig:10 pin numbering scheme}.

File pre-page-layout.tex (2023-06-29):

%A4: 210x297 (BxH)
% \setlength{\voffset}{-2.532 cm}
% \setlength{\hoffset}{-1.57 cm}
\setlength{\voffset}{-2.5 cm}
\setlength{\hoffset}{-2 cm}
% \setlength{\topmargin}{2.0 cm} \setlength{\topskip}{0.1 cm}
\setlength{\topmargin}{1.5 cm}
\setlength{\topskip}{0.1 cm}
\setlength{\evensidemargin}{1.5 cm}
\setlength{\oddsidemargin}{1.5 cm}
%  \setlength{\textwidth}{16.5 cm}
\setlength{\textwidth}{16.0 cm}
\setlength{\footskip}{40pt}
\setlength{\textheight}{24.7cm}
% \setlength{\textheight}{23.5 cm}
\setcounter{page}{1}
\setlength{\parindent}{0cm}
\setlength{\headsep}{20pt}
%------------------ Schrifttyp in der Kopf- und Fusszeilen-------------
\setkomafont{pageheadfoot}{\footnotesize\sffamily}
%----------------------------------------------------------------------
%----------------------------------------------------------------------
% Linien in der Kopf- und Fußzeile
%\renewcommand{\headrulewidth}{0.0pt}   %Linie in der Kopfzeile mit 0.0pt keine Linie
%%\renewcommand{\footrulewidth}{0.0pt}   %Linie in der Fußzeile mit 0.0 pt keine Linie
%\renewcommand{\headrulewidth}{0.2pt}   %Linie in der Kopfzeile mit 0.0pt keine Linie
%\renewcommand{\footrulewidth}{0.2pt}   %Linie in der Fußzeile mit 0.0 pt keine Linie
%----------------------------------------------------------------------
%\renewcommand{\normalfont}{\sffamily} %für die Überschriften
%\renewcommand{\chaptermark}[1]{\markboth{\chaptername\ \thechapter #1}{}}
%\renewcommand{\sectionmark}[1]{\markright{\thesection\ #1}}
% \rfoot{\leftmark\\\rightmark}

%Definitionen für Kopfzeile
% bei documentclass {report} hat der Eintrag für die [gerade Seite] keine Wirkung
%----------------------------------------------------------------------
%%

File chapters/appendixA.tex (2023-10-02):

\chapter{Appendix A}\label{sec:appendix a}
    \include{chapters/bom}
    \newpage
    % ===================================================================================
    \begin{figure}[ht]
        \centering
        
        \caption[Photograph of the full assembly]{Photograph of the full assembly. Fused, filtered and switchable mains voltage plug (1), Raspberry Pi 4 B (2), BigTreeTech Octopus 1.1 with 2 x TMC2209 stepper drivers (3), \qty{24}{\volt} \qty{150}{\watt} PSU (4), \qty{5}{\volt} \qty{25}{\watt} PSU (5), XRS (6), detector stage drive (7), sample stage drive (8), \textit{XRS-A} detector unit (9), detector and sample stages (10).}%
        \label{fig:non boxed full assembly}
    \end{figure}
    \newpage
    % ===================================================================================
    \begin{figure}[ht]
        \centering
        \includesvg[width=.8\textwidth]{drawings/sample_stage_-_exploded}%
        \caption[Sample stage exploded view]{Sample stage exploded view.}%
        \label{fig:sample stage exploded}%
    \end{figure}
    \newpage
    % ===================================================================================
    \begin{figure}[ht]
        \centering
        \includesvg[width=.8\textwidth]{drawings/sample_drive_dimetric.svg}%
        \caption[Sample drive]{Sample drive.}%
        \label{fig:sample drive}%
    \end{figure}
    \newpage
    % ===================================================================================
    \begin{figure}[ht]
        \centering
        \includesvg[width=.7\textwidth]{pictures/footage/interface_front}
        \caption[Top view of the SBC-to-XRS interface board]{Top view of the SBC-to-XRS interface board. DAC in yellow (1), ADC in purple (2).}%
        \label{fig:top view interface board}
    \end{figure}
    \newpage
    % ===================================================================================
    \begin{figure}[ht]
        \centering
        \includesvg[height=.92\textheight]{electronics/pdf/xmagix_peripherals}
        \caption[Schematics of all electronic peripherals]{Schematics of all electronic peripherals.}%
        \label{fig:schematics of peripherals}
    \end{figure}
    \newpage
    % ===================================================================================
    \begin{figure}[ht]
        \centering
        \includesvg[height=.92\textheight]{electronics/pdf/xmagix_peripherals-raspberry4b}
        \caption[Schematics of the GPIO pin assignments]{Schematics of the GPIO pin assignments.}%
        \label{fig:schematics of raspberry gpio configuration}
    \end{figure}
    \newpage
    % ===================================================================================
    \begin{figure}[ht]
        \centering
        \includesvg[width=.9\textwidth]{electronics/sim/LT1009}
        \caption[Simulation of the trim-resistor value dependent behavior of the \textit{LT1009} voltage reference]{Simulation of the trim-resistor value dependent behavior of the \textit{LT1009} voltage reference. At \(R_2 \approx 0\) the value output voltage is \(\approx \qty{2.385}{\volt}\).}%
        \label{fig:LT1009 sim}
    \end{figure}
    \newpage
    % ===================================================================================
    \begin{figure}
        \centering
        \begin{subfigure}{.3\textwidth}
            
            \caption[Set point of \qty{10}{kV} and \qty{1100}{\micro\ampere}]{Set point of \qty{10}{kV} and \qty{1100}{\micro\ampere}.}%
            \label{subfig:12WattController 10kV}
        \end{subfigure}
        \hspace{10mm}
        \begin{subfigure}{.3\textwidth}
            \centering
            
            \caption[Set point of \qty{70}{kV} and \qty{50}{\micro\ampere}]{Set point of \qty{70}{kV} and \qty{50}{\micro\ampere}.}%
            \label{subfig:12WattController 70kV}
        \end{subfigure}
        \caption[XRS GUI tool running on Windows]{XRS GUI tool running on Windows. (a) the filament current maxes out at \(\approx \qty{1100}{\micro\ampere}\). (b) a maximum acceleration voltage of \(\approx\qty{70}{\kilo\volt}\). In any case, the device does not allow exceeding a maximum power of \qty{12}{\watt}.}%
        \label{fig:12WattController 10kV and 70kV}
    \end{figure}
    \newpage
    % ===================================================================================
    \begin{figure}[t]
        \centering
        
        \caption[XRS' analog control pin numbering scheme.]{XRS' analog control pin-numbering scheme.}%
        \label{fig:10 pin numbering scheme}
    \end{figure}
    \newpage
    % ===================================================================================

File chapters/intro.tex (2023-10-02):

\chapter{Introduction}\label{chap:intro}
\nomenclature[A]{XRF}{X-Ray Fluorescence}%
\nomenclature[A]{XRD}{X-Ray Diffraction}%
\nomenclature[A]{SXTM}{Scanning X-Ray Transmission Microscopy}%
\nomenclature[A]{SDD}{Silicon Drift Detector}%
\nomenclature[A]{RPi}{Raspberry Pi}%
\nomenclature[A]{XRS}{X-Ray Source}%
\nomenclature[A]{SBC}{Single Board Computer}%
\nomenclature[A]{DAC}{Digital-to-Analog Converter}%
\nomenclature[A]{ADC}{Analog-to-Digital Converter}%
\nomenclature[A]{LSB}{Least Significant Bit}%
\nomenclature[A]{MSB}{Most Significant Bit}%
\nomenclature[A]{NC}{Normal Closed}%
%
\nomenclature[L]{UNOB}{Unusable Number Of Bits\nomunit{\bit}}%
% \nomenclature[L]{\(E_{Kin}\)}{Kinetic Energy\nomunit{\electronvolt}}%
% \nomenclature[L]{\(E_{\gamma}\)}{Photon Energy\nomunit{\electronvolt}}%
% \nomenclature[L]{\(\hbar\)}{Reduced Planck constant\nomunit{\joule\second}}%
% \nomenclature[L]{\(c\)}{Speed of Light\nomunit{\metre\per\second}}%
\nomenclature[L]{\(I\)}{Electric current\nomunit{\ampere}}%
\nomenclature[L]{\(U\)}{Voltage\nomunit{\volt}}%
\nomenclature[L]{\(U\)}{Voltage\nomunit{\volt}}
\nomenclature[L]{\(res_{\theta}\)}{Angular resolution sample stage\nomunit{\degree\per\step}}
\nomenclature[L]{\(res_{\varphi}\)}{Angular resolution detector stage\nomunit{\degree\per\step}}
%
\nomenclature[G]{\(\lambda\)}{Photon wavelength\nomunit{\nano\metre}}%
\nomenclature[G]{\(\theta\)}{Incident angle\nomunit{1}}%
\nomenclature[G]{\(\varphi\)}{Detector position angle\nomunit{1}}%

Throughout various disciplines the capability for fast elemental or structural analysis is highly desirable.
Nowadays, this typically takes place by irradiating a specimen with x-ray photons and capturing photons ``coming back''.
At the very core of any such device is a source of x-ray photons (XRS) and some arrangement to detect, differentiate and classify incoming photons.\par\medskip

Already at hand: XRS-A, TUB00154-A-06, SBC (RPi)

All this 
    \section{XRF/XRD Working Principles}\label{sec:working principles}

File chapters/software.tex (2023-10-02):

\chapter{Software}\label{chap:software}
    \section{Environment Preparation}\label{sec:env preperation}
        The central component of the \textit{XRS-A} is the digital pulse processor \textit{microDXP} manufactured by \textsc{XIA LLC}.
        \textsc{XIA} provides USB drivers and a GUI tool \textit{ProSpect} for Windows but no pre-compiled binaries for Linux systems.
        The sources for the software API\nomenclature[A]{API}{Application Programming Interface} \textit{Handel} however are provided on their public repository on \textsc{GitHub}~\cite{Software.HandelRelease.2023} and are forked by the author of this work~\cite{Software.XraythesisHandel.2023}.
        As stated in \textit{Handel}'s API documentation \textquote{Handel is a framework of several libraries that interact to create the interface Handel provides}~\cite{Manual.HandelAPIManual.Xiang}.
        As such, all routines not part of that top-level framework are considered lower layers of \textit{Handel}'s API and will not be subject of this work.
        The utilized detector incorporates the \textit{microDXP} as its digital pulse processor, thus, all non-\textit{microDXP} routines will not be discussed here as well.\par\medskip

        \subsection{Building Handel's API Libraries}\label{sec:software preperations}
            The SBC runs the latest x64 version of \textit{Raspberry Pi OS Lite}\footnote{Installed using the \textit{Raspberry Pi Imager} tool.
            Direct download available under~\cite{Software.RaspberryPiOSLite.2023}}.
            A detailed description and troubleshooting suggestions can be found on the author's repository~\cite{Software.XraythesisHandel.2023}.\par\medskip

            \textit{Handel} is meant to be built using \textit{SCons}~--~\textquote{a computer software build tool} which in turn is written in python.
            Thus, it is dependent on a working python environment.
            While Raspberry Pi OS has a Python interpreter pre-installed, its version does not match \textit{SCons} requirements.
            Not only to ensure a consistent and reproducible development environment but also to keep the Python environment isolated from the system, a forked version of \textit{miniconda}\footnote{\textquote{A small bootstrap version of Anaconda that includes only conda, Python, the packages they both depend on, and a small number of other useful packages}}~--~\textit{miniforge}~--~is used.
            As of the time of writing, Miniconda does not provide a build working on arm64 architecture.

            With a working conda install set up, a virtual environment is created, installing a specific Python version~\num{3.9} and activated afterwards following \cref{lst:creating conda env}.
            Next, the required Python packages are installed as well as~--~if not already bundled with the \textit{Raspberry Pi OS} install~--~the \texttt{libusb-dev} libraries.
            \begin{lstlisting}[style=mybash,
                caption={[Creating conda environment and installing dependencies]Creating conda environment and installing dependencies.},
                label={lst:creating conda env}]
    # Create conda environment
    conda create -n xmagix python=3.9 pip ipykernel
    conda activate xmagix

    # Install required python packages
    pip install -r requirements.txt

    # Install other dependencies
    sudo apt install libusb-dev
            \end{lstlisting}

            The main entry point is the shell script \texttt{./build.sh}\footnote{See~\cite{Software.XraythesisHandel.2023} for a list of other/more build options.}.
            To start the build process, it needs to be made executable and executed using the commands shown in~\cref{lst:build.sh}.
            A build log will be created in \texttt{./build.log} and the default build location is \texttt{./myapp/lib/}.
            \begin{lstlisting}[style=mybash, caption={[Executing build script]Executing build script.}, label={lst:build.sh}]
    # Make script executable
    chmod +x ./build.sh

    # Build
    ./build.sh
            \end{lstlisting}
        \subsection{Permissions and Preparing USB}\label{sec:permissions and preparing usb}
            After the detector is plugged into one of the USB ports and is powered up, issuing
            \begin{lstlisting}[style=mybash, numbers=none, label={lst:lsusb}]
    lsusb | grep "ID 10e9"
            \end{lstlisting}
            checks that \textit{libusb} sees the XIA device.
            Next, \texttt{udev} rules need to be put in place to grant user-level access to the USB device.
            The logged-in user should be part of the \texttt{plugdev} group by default.
            If the command
            \begin{lstlisting}[style=mybash, numbers=none, label={lst:get plugdev group}]
    groups | grep "plugdev"
            \end{lstlisting}
            checks if that is true and
            \begin{lstlisting}[style=mybash, numbers=none, label={lst:get plugdev group}]
    sudo usermod -a plugdev <user>
            \end{lstlisting}
            adds the user to the \texttt{plugdev} group if not already the case.
            Issuing
            \begin{lstlisting}[style=mybash, numbers=none, label={lst:udev}]
    sudo echo 'ACTION=="add", SUBSYSTEM=="usb", ATTR{idVendor}=="10e9", ATTRS{idProduct}=="0b01", MODE="0660", GROUP="plugdev"' | sudo tee /etc/udev/rules.d/99-xia.rules
    sudo /etc/init.d/udev restart
            \end{lstlisting}
            creates the file \texttt{/etc/udev/rules.d/99-xia.rules} containing a custom \texttt{udev} rule and restarts the \texttt{udev} daemon\footnote{See~\cite{Software.XraythesisHandel.2023} for a non-comprehensive troubleshooting guide.}~\cite{Software.HandelRelease.2023,Software.XraythesisHandel.2023}.

    \clearpage
    \section{Detector Interface Class}\label{sec:detector interface}
        The main language chosen to interface with the created shared object (\texttt{*.so}) libraries is Python, using the same environment created in~\cref{lst:creating conda env}.
        The class \texttt{XMagix} defined in \texttt{./myapp/xmagix.py} exposes most of the relevant functions of the \textit{Handel} API and is mostly written in plain Python.
        The only external packages loaded are \textit{Numpy} and \textit{Rich}, the former to enable fast matrix manipulation and the latter to auto-timestamp and colorize logging prints to console.\par\medskip

        Furthermore, to actually develop wrapping code, Pythons standard library \textit{ctypes} was used to access \textit{Handel}'s C-functions.
        Following, only the most relevant methods of \texttt{XMagix} are shown.
        See~\cref{lst:xmagix class} for a full overview.\par\medskip

        All of \textit{Handel}'s top-level functions are named camel case and begin with ``xia''~--~they shall be hereafter called xia-functions.
        The Python-wrapped methods adopt their naming scheme but omit ``xia'' e.g. \textit{Handel}'s API function \texttt{xiaInit(inifile)} is exposed as \texttt{<class object name>.init(inifile)}.
        Any call to an xia-function takes either a value of type \texttt{c\_int()} to specify the detector channel (in this case always \texttt{0} as there is only one detector present), an ascii-encoded byte-stream representing an instruction and a reference to a predefined \textit{ctype}-variable either holding a value to set or to receive a value retrieved by the particular xia-function.
        \texttt{XMagix}'s method \texttt{stringToBytes()} takes a \texttt{str}-object as an input and returns a byte-stream.
        Practical examples are shown in \crefrange{sec:init}{sec:pullMcaData}.

        \lstinputlisting[style=mypython, firstnumber=13, caption={[XMagix class constructor]XMagix class constructor.}, label={lst:xmagix constructor}, firstline=13, lastline=27]{software/xmagix.py}
        The constructor of \texttt{XMagix}, as shown in~\cref{lst:xmagix constructor}, besides pre-setting some internal state variables, loads the shared object library from the path passed to it during object creation.
        
        \subsection{init()}\label{sec:init}
            With the detector came a \texttt{*.ini}-file holding values and variables pre-defined by the manufacturer and specific to that particular device.
            \textit{Handel} expects it to be loaded prior to starting up the system.
            One does not need to modify any of its values except the line defining the \texttt{device\_number}.
            \texttt{device\_number} tells \textit{Handel} which USB device to communicate with.\par\medskip

            \lstinputlisting[style=mypython, firstnumber=67, caption={[XMagix method init()]XMagix method init().}, label={lst:xmagix init}, firstline=67, lastline=72]{software/xmagix.py}
        
        \subsection{startSystem()}\label{sec:startSystem}
            After initializing the system using the method described in~\cref{sec:init}, the system can be started up using \texttt{<class object name>.startSystem()}.
            No error codes printed to the console indicates a successful start-up\footnote{\texttt{4001, DXP\_MDOPEN} might indicate a wrong \texttt{device\_number}. If there is more than one USB device plugged into the SBC one might try setting \texttt{device\_number} to an integer value > \texttt{0}.}.\par\medskip

            \lstinputlisting[style=mypython, firstnumber=80, caption={[XMagix method startSystem()]XMagix method startSystem().}, label={lst:xmagix startSystem}, firstline=80, lastline=87]{software/xmagix.py}

        \subsection{setAcquisitionValues()}\label{sec:setAcquisitionValues}
            The method \texttt{setAcquisitionValues()} has two positional arguments: the name of a value to set and the desired value itself.
            The name will be checked against a list of allowed names specified in Appendix A of \textit{Handel's programmer guide}~\cite{Manual.HandelProgrammersGuideMicroDXP.Xiang} and the value stored in the volatile memory if the check returns no error.\par\medskip

            This way the user is able to quickly vary different acquisition values like \texttt{gain\_trim} or any of the filter thresholds.\par\medskip

            \lstinputlisting[style=mypython, firstnumber=98, caption={[XMagix method setAcquisitionValues()]XMagix method setAcquisitionValues().}, label={lst:xmagix setAcquisitionValues}, firstline=98, lastline=108]{software/xmagix.py}
        
        \subsection{getAcquisitionValues()}\label{sec:getAcquisitionValues}
            To retrieve a particular~--~or all~--~currently set acquisition value, \texttt{getAcquisitionValues(<name>)} can be used.
            The method returns a dictionary where the key-value pair reflects the specified name(s) and value(s).\par\medskip

            \lstinputlisting[style=mypython, firstnumber=110, caption={[XMagix method getAcquisitionValues()]XMagix method getAcquisitionValues().}, label={lst:xmagix getAcquisitionValues}, firstline=110, lastline=132]{software/xmagix.py}
        
        \subsection{startRun()}\label{sec:startRun}
            The acquisition value \texttt{"preset\_type"} lets the user choose between five modes of data acquisition runs:
            \begin{itemize}
                \item \texttt{"XIA\_PRESET\_NONE"}~--~starts a run until stopped by the user.
                \item \texttt{"XIA\_PRESET\_FIXED\_REAL"}~--~stops after \texttt{"preset\_value"} seconds.
                \item \texttt{"XIA\_PRESET\_FIXED\_LIVE"}~--~stops after \texttt{"preset\_value"} seconds \(+\) the sum of dead times.
                \item \texttt{"XIA\_PRESET\_FIXED\_EVENTS"}~--~stops after \texttt{"preset\_value"} output events.
                \item \texttt{"XIA\_PRESET\_FIXED\_TRIGGERS"}~--~stops after \texttt{"preset\_value"} trigger events.
            \end{itemize}
            Having a \texttt{"preset\_type"} and corresponding \texttt{"preset\_value"} set, \texttt{startRun()} initiates data acquisition.\par\medskip

            \lstinputlisting[style=mypython, firstnumber=191, caption={[XMagix method startRun()]XMagix method startRun().}, label={lst:xmagix startRun}, firstline=191, lastline=200]{software/xmagix.py}

        \subsection{fixedRealtimeRun()}\label{sec:fixedRealtimeRun}
            To directly start a fixed realtime run, the method \texttt{fixedRealtimeRun()} takes the desired realtime in seconds as a mandatory argument.
            The optional argument \texttt{clearMca}, if set to \texttt{True} (default), clears the internal multichannel analyzer's bins prior starting the run.
            During the data acquisition, alongside the elapsed and total time, basic statistics like output count rate (OCR)\nomenclature[A]{OCR}{Output Count Rate} and the sum of all output events during the run (EIR)\nomenclature[A]{EIR}{Events In Run} are printed to the console in intervals of \qty{1}{\second}.\par\medskip

            \lstinputlisting[style=mypython, firstnumber=202, caption={[XMagix method fixedRealtimeRun()]XMagix method fixedRealtimeRun().}, label={lst:xmagix fixedRealtimeRun}, firstline=202, lastline=232]{software/xmagix.py}

        \subsection{stopRun()}\label{sec:stopRun}
            A call to \texttt{stopRun()} stops any active run.\par\medskip

            \lstinputlisting[style=mypython, firstnumber=234, caption={XMagix method stopRun()}, label={lst:xmagix stopRun}, firstline=234, lastline=244]{software/xmagix.py}

        \subsection{pullMcaData()}\label{sec:pullMcaData}
            After a successful run the data is stores in the \textit{microDXP}'s multichannel analyzer (MCA)\nomenclature[A]{MCA}{MultiChannel Analyzer}.
            \texttt{pullMcaData()} writes the MCA's content to a pre-defined array of length \texttt{nmca} and type \texttt{c\_ulong} and returns it as a \textit{numpy} array without clearing the MCA's content.

            \texttt{nmca} is the length of the MCA i.e.~the number of bins (see~\cref{sec:setAcquisitionValues} and~\cref{sec:getAcquisitionValues}).
            Since each bin can hold a maximum number of \(2^{24} - 1 = 16777215\) events, the arrays \textit{ctype} has to be sufficiently large.\par\medskip

            \lstinputlisting[style=mypython, firstnumber=246, caption={[XMagix method pullMcaData()]XMagix method pullMcaData().}, label={lst:xmagix pullMcaData}, firstline=246, lastline=256]{software/xmagix.py}

    \clearpage
    \section{X-Ray Source Interface Class}\label{sec:xrs interface class}
        Both the ADC and the DAC utilize the SPI protocol, of which the \textit{Raspberry Pi 4 B} has implemented a total of seven hardware buses with two hardware chip-selects each.
        With only two peripheral devices attached to the bus~--~the ADC and the DAC~--~only a single bus is needed.
        Here, the default bus \textit{SPI0} is chosen where the physical pin assignment can be seen in~\cref{fig:schematics of raspberry gpio configuration} and is tabulated in~\cref{tab:gpio assignment} for quick reference.

        To gain access to the SBC's GPIO and activate the hardware SPI peripheral, the SBC needs to be configured accordingly.
        \begin{lstlisting}[style=mybash,numbers=none, caption={[Activating SPI0 and installing \texttt{pigpio}]Activating SPI0 and installing \texttt{pigpio}. Enabling the system service ensures automatic start up after boot.},label={lst:SPI0 and pigpio}]
            # Enable SPI0 using raspi-config in non-interactive mode
            sudo raspi-config nonint do_spi 0

            # Install fast GPIO library and activate/start service
            sudo apt-get update
            sudo apt-get install pigpio python-pigpio python3-pigpio
            sudo systemctl enable pigpiod.service
            sudo systemctl start pigpiod.service
        \end{lstlisting}
        \Cref{lst:SPI0 and pigpio} utilizes any \textit{Raspberry Pi OS's} built-in tool \texttt{raspi-config} in non-interactive mode to quickly activate the SPI on bus 0.
        After that, \textit{pigpio}, a tool for fast GPIO usage, is installed and its system service is enabled to ensure automatic start up in case the host system is rebooted.
        From \cref{sec:electronics} and with \cref{fig:schematics of raspberry gpio configuration} the pin assignments are tabulated in \cref{tab:gpio assignment} for further reference.

        \begin{table}[h]
            \centering
            \caption[Pin assignment of the SBC's GPIO]{Pin assignment of the SBC's GPIO.}%
            \label{tab:gpio assignment}
            \begin{tabular}{@{}lll@{}}
                \toprule
                Function&           Broadcom Pin Name&  Bus Device\\
                \midrule
                MOSI&	            GPIO10&\\
                MISO&	            GPIO09&\\
                SCLK&	            GPIO11&\\
                CE0&	            GPIO08&             ADC\\
                CE1&	            GPIO07&             DAC\\
                Filament Ready&     GPIO24&\\
                HV/Filament Enable& GPIO25&\\
                \bottomrule
            \end{tabular}
        \end{table}

        \subsection{Initializing the SPI Bus}\label{sec:init spi bus}
            The Python class \texttt{Tube} implements automatic initialization of the SPI bus and allows easy reading from and writing to the XRS.
            While doing so, it has to adhere to the SPI protocol description and timing requirements of the two different devices connected to the bus.
            Lines 9 to 17 of the constructor shown in \cref{lst:Tube constructor} set the pin modes of GPIO24 and GPIO25 responsible i.e. \texttt{Filament Ready} and \texttt{HV/Filament Enable} pins\footnote{Although the full code can be found in~\cref{lst:Tube full source}, reading and writing specific GPIO pins is considered trivial and will not be further elaborated.}.
            Line 19 to 24 configure the SPI modes for the DAC and the ADC respectively.
            The three arguments of \texttt{spi\_open} set the channel (the \(\overline{\texttt{CS}}\) pin the device is physically connected to), the Baud (clock speed) and the mode.

            \begin{figure}[h]
                \centering
                \includesvg[width=.8\textwidth]{electronics/datasheets/tlv5618_timing_req}
                \caption[TLV5618a timing requirements]{TLV5618a timing requirements~\cite{Manual.DAC.TLV5618A}. A bit is read on the falling edge at the end of a clock pulse with the clock idling low which translates to clock polarity 0 and clock phase 1.}
                \label{fig:tlv5618a timing req}
            \end{figure}\par\medskip

            Clock polarity defines the idle state of the clock, thus, the clock's logic level while \(\overline{\texttt{CS}}\)\footnote{\texttt{CS}\nomenclature[A]{CS}{Chip Select} i.e. Chip Select is synonym with \texttt{CE}\nomenclature[A]{CE}{Chip Enable} i.e. Chip Enable.} is logic high.
            Clock phase defines when a bit is being sampled.
            \Cref{fig:tlv5618a timing req} is taken from the DAC's datasheet and shows that the DAC is compatible with either clock polarities and samples a bit on the clocks transition to idle, making it compatible with SPI modes 1 and 2~\cite{Manual.IntroductionToSPIInterface.Dhaker.SPI}.
            Further, it operates at a clock speed of \qty{20}{\mega\hertz} and is physically connected to \(\overline{\texttt{CS1}}\).
            Line 19 in~\cref{lst:Tube constructor} shows the final composition of the arguments necessary for \texttt{spi\_open}~\cite{Manual.PigpioLibrary}.\par\medskip

            The ADC communicates at \qty{100}{\kilo\hertz} on \(\overline{\texttt{CS0}}\) and is compatible with SPI modes 0 and 3.
            To have the clock phases in sync during debugging, SPI modes are chosen such that the clock signal idles low on both devices.

            \lstinputlisting[style=mypython, firstnumber=5,
            caption={[\texttt{Tube} class's constructor]\texttt{Tube} class's constructor.},
            label={lst:Tube constructor}, firstline=5, lastline=28]{software/thetube.py}

            To let the ADC begin sampling the analog signal at its input, it expects a single start bit and three configuration bits after which it starts to clock back one \texttt{NULL} bit followed by its sampling result of 12 bits.
            Aligned with the clock edge transitioning from idle, the receive-buffer starts to fill with random bits immediately after \(\overline{\texttt{CS}}\) is pulled low.
            Following the application information of the \textit{MCP3202} sending a total of 3 bytes consisting of seven leading zeros, the start bit, three configuration bits and 13 \texttt{Don't Care} bits, the receive-buffer will fill with three bytes as well (see \cref{fig:adc communication protocol}), with bit 0 of the last received byte being the least significant bit (LSB) and bit 3 of the second byte the most significant bit (MSB) of the conversion result.
            \begin{figure}[h]
                \centering
                \includesvg[width=.8\textwidth]{electronics/datasheets/mcp3202_protocol}
                \caption[ADC communication protocol]{ADC communication protocol~\cite{Manual.ADC.MCP3202}.}%
                \label{fig:adc communication protocol}
            \end{figure}

            Line 24 in~\cref{lst:Tube constructor} pre-defines the three bytes with leading zeros, start bit, single-ended mode, channel 1 and trailing ones.
            Lines 26 to 28 initialize the two DAC-channels with \qty{0}{\volt} and pull \texttt{enpin} low, disabling the XRS.

            \subsection{enable()}\label{sec:tube enable}
                The method \texttt{enable()} is a shortcut to set \texttt{enpin} high, enabling the acceleration voltage, filament current and setting an internal state variable accordingly.
                The user can use this method and \texttt{disable()} in \cref{sec:tube disable} to programmatically enable and disable the XRS prior and after each data acquisition run.\par\medskip

                {\bfseries Warning: this enables the x-ray source if \texttt{HV Control} (\texttt{setHV()}) and \texttt{Current Control} (\texttt{setI()}) values are set \(> 0\)!}\par\medskip

                \lstinputlisting[style=mypython, firstnumber=34, caption={[\texttt{Tube} method \texttt{enable()}]\texttt{Tube} method \texttt{enable().}}, label={lst:Tube method enable}, firstline=34, lastline=36]{software/thetube.py}

            \subsection{disable()}\label{sec:tube disable}
                Same as~\cref{sec:tube enable} but disabling acceleration voltage and filament current.

                \lstinputlisting[style=mypython, firstnumber=38, caption={[\texttt{Tube} method \texttt{enable()}]\texttt{Tube} method \texttt{disable().}}, label={lst:Tube method disable}, firstline=38, lastline=40]{software/thetube.py}
            
            \subsection{read()}\label{sec:read}
                \texttt{read} takes a single positional argument \texttt{channel} and returns a list containing the raw conversion result from the ADC and a calculated real-world value in \unit{\keV} or \unit{\uA} using the monitor resolutions in~\cref{tab:adc dac performance summery}, depending on the chosen channel.\par\medskip

                \lstinputlisting[style=mypython, firstnumber=68, caption={[\texttt{Tube} method \texttt{read()}]\texttt{Tube} method \texttt{read().}}, label={lst:Tube method read}, firstline=68, lastline=84]{software/thetube.py}

            \subsection{composeBytesDac()}\label{sec:composebytesdac}
                Tube class's internal helper function \texttt{composeBytesDac()} shown in \cref{lst:Tube method composebytesdac} is not supposed to be invoked by user-level methods.
                Its purpose is to pack the desired set points and configuration bits into a 2-byte payload ready to be transmitted to the DAC.
                Hence, it takes two mandatory arguments; the actual value i.e. set point and the target channel, and defaults two optional arguments \texttt{fast} and \texttt{pwr} to \texttt{False} and \texttt{True}.
                The application in this work demands no high-speed output, thus, to ensure better signal integrity by reducing the stability requirements of the reference voltage, fast mode is set to False~\cite{Manual.ADC.MCP3202}.
                \texttt{pwr} sets the on/off state of the device and should normally be kept \texttt{True}.

                \begin{table}[h]
                    \centering
                    \caption[Channel select register bits of the ADC]{Channel select register bits of the ADC~\cite{Manual.DAC.TLV5618A}.}%
                    \label{tab:channel select bits adc}
                    \begin{tabular}{@{}rlll@{}}
                        \toprule
                        & R1& R0& REGISTER\\
                        \midrule
                        \(\rightarrow\)& 0& 0& Write data to DAC B and BUFFER\\
                        & 0& 1& Write data to BUFFER\\
                        \(\rightarrow\)& 1& 0& Write data to DAC A and update DAC B with BUFFER content\\
                        & 1& 1& Reserved\\
                        \bottomrule
                    \end{tabular}
                \end{table}

                Depending on the chosen channel i.e. keyword argument \texttt{channel} = \texttt{True/False}, the channel select register bit \texttt{R1} is set 0 or 1 while keeping \texttt{R0} 0 at all times (see highlighted lines in~\cref{tab:channel select bits adc}~\cite{Manual.DAC.TLV5618A}).\par\medskip

                \lstinputlisting[style=mypython, firstnumber=42,
                caption={[\texttt{Tube} method \texttt{composeBytesDac()}]\texttt{Tube} method \texttt{composeBytesDac().}},
                label={lst:Tube method composebytesdac}, firstline=42, lastline=66]{software/thetube.py}

            \subsection{setHV()}\label{sec:setHV}
                \texttt{setHV()} is a method to translate a desired acceleration voltage in \unit{\kev} to a \qty{12}{\bit} integer value to pass to the DAC's channel 0.
                The user must input a value in a range from \qtyrange{4}{60}{\kev}.
                Values below \qty{4}{\kev} and above \qty{60}{\kev} will be set to 0.
                In any case, the actual set value for the acceleration voltage is stored in a class variable \texttt{hv} for later calculations of the maximum allowed filament current.\par\medskip

                \begin{align}
                    val_{hv,ctrl} = \fint*{ \frac{hv}{res_{hv,ctrl}} }
                    \label{eq:setHV val mapping}
                \end{align}

                Knowing the resolution from~\cref{tab:adc dac performance summery} and assuming a linearity error and offset error of 0,
                the slope of the transfer function can be calculated as shown in~\cref{eq:setHV val mapping} and line 90 below.
                
                \lstinputlisting[style=mypython, firstnumber=86, caption={[\texttt{Tube} method \texttt{setHV()}]\texttt{Tube} method \texttt{setHV().}}, label={lst:Tube method setHV}, firstline=86, lastline=102]{software/thetube.py}

            \subsection{setI()}\label{sec:setI}
                \texttt{setI()} is a method to translate a desired filament current in \unit{\micro\ampere} to a \qty{12}{\bit} integer value to pass to the DAC's channel 1.
                The principle of mapping the desired current to an input value is basically the same as discussed in~\cref{sec:setHV}, but to ensure operating the XRS inside its specification limits the value of argument \(\texttt{i}\) undergoes an extra conditioning step, limiting the output to an appropriate value.

                \begin{align}
                    val_{i,ctrl} = \fint*{ \frac{i}{res_{i,ctrl}} }
                    \label{eq:setI val mapping}
                \end{align}
                \nomenclature[L]{\(val\)}{integer value transmitted to the ADC/DAC\nomunit{1}}

                The XRS is designed to operate at a maximum output power of \qty{12}{\watt}.
                Line 107 in~\cref{lst:Tube method setI} calculates the maximum allowed filament current according to the currently set acceleration voltage and stores it in the local variable \texttt{imax}.
                If that filament current exceeds \qty{1000}{\uA}, line 109 caps it at the XRS' specified maximum filament current.
                Lastly, in line 114, \texttt{i} gets capped off at the value of \texttt{imax} if the user has set it above \texttt{imax}.\par\medskip
                
                \lstinputlisting[style=mypython, firstnumber=104, caption={[\texttt{Tube} method \texttt{setI()}]\texttt{Tube} method \texttt{setI().}}, label={lst:Tube method setI}, firstline=104, lastline=123]{software/thetube.py}

    \clearpage
    \section{Motion System}\label{sec:motion system}
        % Due to the rise of hobby-level 3D-printing not only hardware components became readily available but firmware development as well profited of thriving communities and still does.
        Among managing other important tasks, one of any 3D-printing firmware's most crucial functions is generating precisely timed stepping pulses to drive usually three or more motors at once.
        Since reproducing that functionality is a non-trivial task and due to time limitations, the decision in favor of proven software was made despite it packing far more features than probably needed.
        The popular 3D-printer firmware \textit{Klipper}~\cite{Software.Klipper.2023} was chosen to generate the stepping pulses.
        
        Due to time limitations, no XMagix user interface is yet integration.
        To still be able to drive the motion system, a pre-made 3D-printing web interface \textit{Fluidd}~\cite{Software.FluiddTheKlipperUI} is used instead.
        
        \textit{Fluidd} itself depends on \textit{Moonraker}~\cite{Software.MoonrakerAPIWebServerForKlipper.2023}~--~an intermediate communication layer exposing the low level \textit{Klipper} commands as an API web server.\par\medskip

        Lastly and for the sake of ease of setting all software components up, \textit{kiauh} is used to automate download and installation as well as taking care of any preliminary configuration of necessary services\footnote{As the time of writing the recommended \textit{Klipper} version running on top of Python 3 is non-functional and the legacy Python 2 variant is installed instead.}. Instruction on how to download and use the script can be taken from \textit{kiauh}'s repository~\cite{Software.KlipperInstallationAndUpdateHelper.2023}.\par\medskip

        \textit{Klipper} functions by allocating all demanding computational work to the relatively potent host processor~--~the device it is installed to~--~and shifts only the resulting I/O instructions out to the attached peripheral hardware.
        This requires that hardware to run a daughter software making it understand those instructions.
        \textit{Klipper} comes with a shell script to configure a makefile and build the required binaries.
        In the case of the used \textit{Octopus v1.0}, the microcontroller architecture \texttt{LPC176x} and the processor model \texttt{LPC1769} must be selected.

        \begin{lstlisting}[style=mybash, numbers=none]
    cd ~/klipper
    make menuconfig
        \end{lstlisting}

        Exiting the menu, a file \texttt{\textasciitilde/klipper/.config} will be created configuring the build process initiated after a final invocation of \texttt{make}\footnote{A pre-made config file can be found in~\cref{lst:make config file} for reference.}.\par\medskip

        To flash the built binary to the peripheral hardware and to correctly address it afterwards, \textquote[\cite{Software.Klipper.2023}]{it is necessary to determine the serial port connected to the micro-controller}. With only the stepper driver board and the detector connected to the USB-bus, the following command prints a single output in the way like \texttt{/dev/serial/by-id/<some string>}.

        \begin{lstlisting}[style=mybash, numbers=none]
    ls /dev/serial/by-id/*
        \end{lstlisting}
        
        The following two lines start the flashing procedure and restart \textit{Klipper}'s system service afterwards.
        
        \begin{lstlisting}[style=mybash, numbers=none]
    make flash FLASH_DEVICE=/dev/serial/by-id/<some string>
    sudo systemctl restart klipper
        \end{lstlisting}

        At start of the service \textit{Klipper} reads all parameters needed for the individual setup from the configuration file \texttt{\textasciitilde/printer\_data/config/printer.cfg}.
        The most important portion of the configuration file~--~section \texttt{[mcu]}~--~is shown in~\cref{lst:usb by id}.
        After flashing the binary to the peripheral hardware, the command above re-issued yields a new device file location which \texttt{Klipper} must be pointed to.
        The configuration file needs to be edited accordingly by entering it as a value for \texttt{serial}.
        % With all preliminary configurations in place, entering the IP-address of the host system into a browser of a device 

        \begin{lstlisting}[style=mydjango, firstnumber=7,
            caption={[\texttt{mcu}-section of \texttt{printer.cfg} showing the id of the connected serial device]\texttt{mcu}-section of the \texttt{printer.cfg} showing the id of the connected serial device.},
            label={lst:usb by id}%
            ]
    [mcu]
    serial: /dev/serial/by-id/usb-Klipper_stm32f446xx_440022001251303431333234-if00
        \end{lstlisting}

        Hereafter, the sections \texttt{[stepper\_x]}, \texttt{[stepper\_y]} and \texttt{[stepper\_z]} must be populated for \texttt{Klipper} service to start without error.
        The detector stage will be driven by \texttt{[stepper\_x]}, the sample stage by \texttt{[stepper\_y]}.
        Physically, there is no motor connected to \texttt{[stepper\_z]} so the entries in this section can be filled with dummy values.

        Taking the detector stage as an example~\cref{lst:stepper section printer cfg}, shows all necessary entries.
        The pin definitions are taken from~\cref{tab:octopus pin assignments} and correspond to the physical connections to the board as discussed in~\cref{sec:kinematics}.

        \begin{lstlisting}[style=mydjango, firstnumber=16,
            caption={[Example stepper section of \texttt{printer.cfg}]Example stepper section of \texttt{printer.cfg}.},
            label={lst:stepper section printer cfg}%
            ]
    [stepper_x]
    step_pin: PF13
    dir_pin: PF12
    enable_pin: !PF14
    microsteps: 32
    rotation_distance: 500 # unit mm
    gear_ratio: 250:80
    full_steps_per_rotation: 200
    endstop_pin: ^PG6
    position_endstop: 0 # unit mm
    position_max: 300
    homing_speed: 10 # unit mm/min
    homing_retract_dist: 5 # unit mm
    homing_positive_dir: false
        \end{lstlisting}

        Variables \texttt{rotation\_distance}, \texttt{gear\_ratio} and \texttt{full\_steps\_per\_rotation} define the physical setup of the effector comprising motors and gearing.
        Here, \texttt{gear\_ratio} denotes the ratio of the last gear in the chain (250T attached to the slewing ring) to the very first gear (80T on the motor shaft) ignoring all other gearing in between.
        To achieve the maximum precision on the drivers' end, a microstepping of 32 is chosen, increasing the amount of full steps per revolution by a factor of 32.
        \texttt{rotation\_distance} is the distance in \unit{\milli\meter} traveled after one full rotation of the last gear.
        The detector stage is mechanically not capable of traveling beyond \(\approx \qty{225}{\degree}\).
        With a safety margin, the maximum allowed travel distance of the X-axis is capped at \qty{300}{\milli\metre} along the gears' pitch diameter, which translates to

        \begin{equation}
            \frac{\qty{360}{\degree}}{\qty{500}{\milli\metre}} \cdot \qty{300}{\milli\metre} = \qty{216}{\degree}
            \label{eq:position max}
        \end{equation}
        
        Since each motor is driven by a dedicated \textit{TMC2209} stepper driver, each section defining a physical axis is accompanied by a special \texttt{tmc2209} section (see~\cref{lst:stepper tmc section} for reference).
        The \textit{TMC2209} stepper drivers are capable of interpolating 256 steps between each full step regardless of the actual microstepping mode.
        Whilst this does provide a smoother motion, interpolation mode is more prone to missed steps, requiring a higher motor current to counter its negative effects.
        Additionally, the stepper drivers feature StealthChop2~--~a \textquote{voltage-chopper based principle} to guarantee \textquote{that the motor is absolutely quiet in standstill and in slow motion}~\cite{Manual.TMC2209Datasheet} in trade for more heat generated in the motor windings while reducing torque at any given speed compared to normal operation.
        Since the application in this work does not require exceptionally quiet motion, the threshold for dynamically switching to StealthChop is set to \qty{0}{\milli\metre\per\minute}.
        \begin{lstlisting}[style=mydjango, firstnumber=31,
            caption={[Stepper corresponding stepper driver section of \texttt{printer.cfg}]Stepper corresponding stepper driver section of \texttt{printer.cfg}.},
            label={lst:stepper tmc section}%
            ]
    [tmc2209 stepper_x]
    uart_pin: PC4
    interpolate: False
    run_current: 0.8 # unit A
    sense_resistor: 0.110 # unit Ohm
    stealthchop_threshold: 0 # unit mm/min
        \end{lstlisting}

    \clearpage
    \section{User Interface}\label{sec:user interface}
        As a preliminary user interface putting all software components together, a Jupyter notebook was created and hosted on the SBC itself (see \texttt{./myapp/user.ipynb} in~\cite{Software.XraythesisHandel.2023}).
        Here, both classes \texttt{XMagix} and \texttt{Tube} are loaded and most important functions are exposed inside individual cells separated by logical sectioning.
        In order to have all dependencies available, the kernel inside the conda environment \texttt{xmagix} created in~\cref{sec:software preperations} must be chosen as the executing kernel.
        The following lines executed import the custom classes into the IPython kernel.
        \begin{lstlisting}[style=mypython, firstnumber=auto]
    from xmagix import XMagix
    from thetube import Tube
    tube = Tube()
    xmagix = XMagix("lib/libhandel.so")
        \end{lstlisting}

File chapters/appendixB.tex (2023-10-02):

\chapter{Appendix B}\label{chap:appendix b}
    \lstinputlisting[%
        style=mypython-apx,
        caption={[Full Python code of \texttt{XMagix} class]Full Python code of \texttt{XMagix} class.},
        label={lst:xmagix class}%
        ]{software/xmagix.py}
    \newpage
    % ===================================================================================
    \lstinputlisting[%
        style=mypython-apx,
        caption={[\texttt{XMagix} helper dict \texttt{acquisition\_values}]\texttt{XMagix} helper dict \texttt{acquisition\_values}.},
        label={lst:xmagix helper acquisition values}%
        ]{software/theacquisition_values.py}
    \newpage
    % ===================================================================================
    \lstinputlisting[%
        style=mypython-apx,
        caption={[\texttt{XMagix} helper lists \texttt{CONSTANTS}, \texttt{ACQ\_MEM\_CONSTANNTS} and \texttt{BOARD\_INFO}]\texttt{XMagix} helper lists \texttt{CONSTANTS}, \texttt{ACQ\_MEM\_CONSTANNTS} and \texttt{BOARD\_INFO}.},
        label={lst:xmagix helper constants}%
        ]{software/theapp_constants.py}
    \newpage
    % ===================================================================================
    \lstinputlisting[%
        style=mypython-apx,
        caption={[\texttt{XMagix} helper dict \texttt{ERRORS}]\texttt{XMagix} helper dict \texttt{ERRORS}.},
        label={lst:xmagix helper errors}%
        ]{software/theapp_errors.py}
    \newpage
    % ===================================================================================
    \lstinputlisting[%
        style=mypython-apx,
        caption={[\texttt{XMagix} helper lists \texttt{board\_operations} and \texttt{board\_operations\_all}]\texttt{XMagix} helper lists \texttt{board\_operations} and \texttt{board\_operations\_all}.},
        label={lst:xmagix helper board operations}%
        ]{software/theboardoperations.py}
    \newpage
    % ===================================================================================
    \lstinputlisting[%
        style=mypython-apx,
        caption={[\texttt{Tube} full source]\texttt{Tube} full source.},
        label={lst:Tube full source}%
        ]{software/thetube.py}
    \newpage
    % ===================================================================================
    \lstinputlisting[%
        style=mypython-apx,
        caption={[Pre-made config file to build \textit{Klippers} peripheral binaries]Pre-made config file to build \textit{Klippers} peripheral binaries.},
        label={lst:make config file}%
        ]{software/klipper/.config}
    \newpage
    % ===================================================================================
    \lstinputlisting[%
        style=mydjango,
        caption={[Example \textit{printer.cfg} to configure \textit{Klipper}]Example \textit{printer.cfg} to configure \textit{Klipper}.},
        label={lst:printer.cfg file}%
        ]{software/klipper/printer.cfg}

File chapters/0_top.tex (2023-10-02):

\begin{titlepage}
	\newcommand{\HRule}{\rule{\linewidth}{0.5mm}}
	\centering
	\textsc{\Large RheinMain University of Applied Sciences} \par

	\begin{center}
		\includesvg[width=0.09\textwidth]{logo-hsrm}
	\end{center}
	\textsc{\LARGE \titleLV}\vspace{0.5cm}
	\HRule\vspace{0.6cm}
	{\huge\bfseries \subtitleA}\par\vspace{0.4cm} % Title of Document
	{\huge\bfseries \subtitleB}\par\vspace{0.4cm}
	\HRule\vspace{1.5cm}
	%-------------------
	\begin{minipage}{0.4\textwidth}
		\centering
		\Large
		\textit{\underline{Author}}\par\vspace{0.5cm}
		\textsc{\nameA}\par\vspace{0.25cm}
		\large
		\textsc{Mat.No.: \(1141919\)}\par\vspace{2cm}
	\end{minipage}
	\begin{minipage}{0.6\textwidth}
		\centering
		\large
		{\rule{.5cm}{.1pt}}\par\vspace{0.5cm}
		\textit{Under the Supervision of}\par\vspace{0.5cm}
		\textsc{Daniel Münstermann, Prof.}\par\vspace{0.5cm}
		\textit{and}\par\vspace{0.5cm}
		\textsc{Tobias Wöll, M.Sc.}\par\vspace{0.5cm}
		{\rule[5pt]{.5cm}{.1pt}}
	\end{minipage}
	%------------------------------------
	\vfill\vfill\vfill
	\textsc{\Large Department of Engineering}\par\vspace{0.5cm}\par
	\textsc{\large Bachelor of Science}\par\vspace{0.5cm}
	\textsc{\large Applied Physics}\par\vspace{0.2cm}
	\vfill
	\begin{flushleft}
		Date:\hspace{0.4cm} {\large\today}
	\end{flushleft}
\end{titlepage}

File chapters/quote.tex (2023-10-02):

\thispagestyle{empty}
\vspace*{.25\textheight}
\begin{hyphendisplayquote}{american}
    \centering
    {\Huge I did not think. I investigated.}
    \begin{flushleft}
        {\large \hspace{3cm}-- Röntgen, W.C.}
    \end{flushleft}
\end{hyphendisplayquote}
\vspace*{\fill}

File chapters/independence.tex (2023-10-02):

\chapter*{Declaration of Independence}

    I hereby certify that I have written this thesis independently and without any unauthorized help from third parties.
    The texts taken directly or indirectly from external sources, concepts, etc. in my explanations have been clearly marked as such and with complete references to the respective authorship and source.
    All further contents like text parts, illustrations, tables etc.~--~without corresponding references~--~originate from me in the sense of copyright.

    This thesis has not been published in Germany or abroad in the same or a similar form to any other examination authority.

    I am aware that an attempt to deceive has been made if one of the above assurances proves to be incorrect.\par\vspace{2cm}

% \rule{3cm}{.1pt}\par
{\Large\bfseries\sffamily Eigenständigkeitserklärung}\par\bigskip

    Hiermit versichere ich, dass ich die vorliegende Arbeit selbständig und ohne unzulässige Hilfe Dritter verfasst habe.
    Die aus fremden Quellen direkt oder indirekt übernommenen Texte, Gedankengänge, Konzepte usw. in meinen Ausführungen habe ich als solche eindeutig gekennzeichnet und mit vollständigen Verweisen auf die jeweilige Urheberschaft und Quelle versehen.
    Alle weiteren Inhalte wie Textteile, Abbildungen, Tabellen etc. ohne entsprechende Verweise stammen im urheberrechtlichen Sinn von mir.

    Die vorliegende Arbeit wurde bisher weder im In- noch im Ausland in gleicher oder ähnlicher Form einer anderen Prüfungsbehörde vorgelegt.

    Mir ist bekannt, dass ein Täuschungsversuch vorliegt, wenn sich eine der vorstehenden Versicherungen als unrichtig erweist.

    \begin{minipage}[!h]{.8\textwidth}
        \par\vspace{1.2cm}
        \hspace{.5cm}Mainz, \today\hspace{.6cm} \includesvg[width=2.5cm]{sig}\par\vspace{.4cm}
        {\hspace{.5cm}\textit{City, Date and Signature of the Author}}
    \end{minipage}

\clearpage

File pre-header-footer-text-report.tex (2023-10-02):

% le --> links, gerade Seite
% ce --> mittig, gerade Seite
% re --> rechts, gerade Seite
% lo --> links, ungerade Seite
% co --> mittig, ungerade Seite
% ro --> rechts, ungerade Seite
% even --> gerade Seite
% odd --> ungerade Seite
%----------------------------------------- Header
\newcommand{\titelkopfzeilemitteeven}{}
\newcommand{\titelkopfzeilemitteodd}{}
\newcommand{\titelkopfzeilelinkseven}{RheinMain University of Applied Sciences}
\newcommand{\titelkopfzeilelinksodd}{RheinMain University of Applied Sciences}
\newcommand{\titelkopfzeilerechtseven}{\nameA}
\newcommand{\titelkopfzeilerechtsodd}{\nameA}
%----------------------------------------- Footer
\newcommand{\titelfusszeilemitteeven}{}
\newcommand{\titelfusszeilemitteodd}{}

\newcommand{\titelfusszeilerechtseven}{Applied Physics}
\newcommand{\titelfusszeilerechtsodd}{\thepage \hspace{0.5mm} of \pageref{LastPage}}
\newcommand{\titelfusszeilelinkseven}{\thepage \hspace{0.5mm} of \pageref{LastPage}}
\newcommand{\titelfusszeilelinksodd}{Applied Physics}

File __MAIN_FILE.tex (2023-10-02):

\documentclass[paper=a4,11pt,titlepage,twoside=false,headings=normal,numbers=noenddot,captions=tableabove,listof=totoc,index=totoc,bibliography=totoc]{scrreprt}
%-----------------------------------------------------------------
\usepackage{etoolbox}
% \booltrue{deutsch}	% comment out to switch document to english
%-----------------------------------------------------------------
\input{pre-variables}
\input{pre-packages}
\input{pre-page-layout}
\input{pre-header-footer-2010}
\input{pre-header-footer-text-report}
\input{pre-listings-layouts}
\input{pre-nomenclature-layout}
\DeclareNameAlias{author}{family-given}
\DeclareNameAlias{editor}{family-given}
\DeclareNameAlias{translator}{family-given}
\addbibresource{lib/literature.bib}
%------DEBUGGING--------------------------------------------------
% \usepackage[showframe]{geometry} % comment for live version
% \usepackage{layout}
% \usepackage{showframe}
\begin{document}
%-----------------------------------------------------------------
\input{chapters/0_top}
\input{chapters/blank}
\input{chapters/independence}
\input{chapters/quote}
\tableofcontents
\printnomenclature[5cm]
%-----------------------------------------------------------------
\clearpage
\pagenumbering{arabic}
% \include{chapters/motivation}
\include{chapters/intro}
\include{chapters/hardware}
\include{chapters/software}
\include{chapters/testing_and_characterization}
\include{chapters/conclusions}
%-----------------------------------------------------------------
\newpage
% \setcounter{page}{5}
% \pagenumbering{roman}
\appendix
% \pagenumbering{Roman}
\input{chapters/appendixA}
\input{chapters/appendixB}
% \clearpage
% \pagenumbering{Roman}
\listoffigures
\listoftables
\lstlistoflistings
\printbibliography[notkeyword={software}]%
\printbibliography[keyword={software}, title={Software}]%
%=================================================================
\end{document}

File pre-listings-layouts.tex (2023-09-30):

%
%=====================Code Listing Layout Matlab=============================
\definecolor{codegreen}{RGB}{28,172,0} % color values Red, Green, Blue
\definecolor{codedarkgreen}{RGB}{94,153,85}
\definecolor{codelilas}{RGB}{170,55,241}
\definecolor{codeorange}{RGB}{155, 55, 31}
\definecolor{codegrey}{rgb}{0.6,0.6,0.6}
\lstdefinestyle{mypython}{
    language=Python,
    tabsize=1,
    postbreak=\mbox{\textcolor{red}{$\hookrightarrow$}\space},
    basicstyle=\ttfamily\footnotesize,
    inputencoding=utf8,
    breaklines=true,
    stepnumber=1, % line numbering steps
    % morekeywords={ones,height,width,datetime}, % additional keywords to highlight
    keywordstyle=\color{blue},
    frame=none,
    identifierstyle=\color{black},
    stringstyle=\color{codeorange},
    commentstyle=\color{codegreen},
    showstringspaces=false, %without this there will be a symbol in the places where there is a space
    numbers=left,
    numberstyle={\tiny \color{black}}, % size of the numbers
    numbersep=-6pt % this defines how far the numbers are from the text
}
\lstdefinestyle{mypython-apx}{
    language=Python,
    tabsize=1,
    postbreak=\mbox{\textcolor{red}{$\hookrightarrow$}\space},
    basicstyle=\ttfamily\footnotesize,
    inputencoding=utf8,
    breaklines=true,
    stepnumber=1, % line numbering steps
    % morekeywords={ones,height,width,datetime}, % additional keywords to highlight
    keywordstyle=\color{blue},
    frame=none,
    identifierstyle=\color{black},
    stringstyle=\color{codeorange},
    commentstyle=\color{codegreen},
    showstringspaces=false, %without this there will be a symbol in the places where there is a space
    numbers=left,
    numberstyle={\tiny \color{black}}, % size of the numbers
    numbersep=5pt % this defines how far the numbers are from the text
}
\lstdefinestyle{mydjango}{
    language=Python,
    tabsize=1,
    postbreak=\mbox{\textcolor{red}{$\hookrightarrow$}\space},
    basicstyle=\ttfamily\footnotesize,
    inputencoding=utf8,
    breaklines=true,
    stepnumber=1, % line numbering steps
    morekeywords={
        include,
        mcu,
        printer,
        virtual_sdcard,
        stepper_x,
        tmc2209,
        stepper_y,
        stepper_z,
        homing_override,
        force_move,
        gcode_macro,
        idle_timeout
        }, % additional keywords to highlight
    keywordstyle=\color{blue},
    frame=none,
    identifierstyle=\color{black},
    stringstyle=\color{codeorange},
    commentstyle=\color{codegreen},
    showstringspaces=false, %without this there will be a symbol in the places where there is a space
    numbers=left,
    numberstyle={\tiny \color{black}}, % size of the numbers
    numbersep=5pt % this defines how far the numbers are from the text
}
\lstdefinestyle{mybash}{
    language=sh,
    tabsize=1,
    postbreak=\mbox{\textcolor{red}{$\hookrightarrow$}\space},
    basicstyle=\ttfamily\footnotesize,
    inputencoding=utf8,
    breaklines=true,
    stepnumber=1, % line numbering steps
    morekeywords={lsusb,grep,sudo,echo,conda,pip,chmod,tee,apt,groups,ls,make}, % additional keywords to highlight
    keywordstyle=\color{blue},
    frame=none,
    identifierstyle=\color{black},
    stringstyle=\color{codeorange},
    commentstyle=\color{codegreen},
    showstringspaces=false, %without this there will be a symbol in the places where there is a space
    numbers=left,
    numberstyle={\tiny \color{black}}, % size of the numbers
    numbersep=-6pt % this defines how far the numbers are from the text
}
%==============================================================================

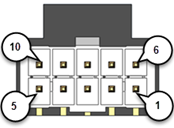
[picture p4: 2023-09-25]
electronics/datasheets/XRS_10pin_male.png

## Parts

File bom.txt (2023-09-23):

Pos.    Menge   Benennung
1	1		Sample Platform
2	1		Sample Driven Gear 80T
3	2		SKF_W 61708.stp
4	1		Stator Center
5	1		Stator Center Spac
6	1		Motor Mounnt Sample Dr
7	2		17HM19-2004S
8	2		Belt Tightener
9	32		DIN 934 M5 Hex Nut
10	44		DIN 912 M5 x 25
11	8		Washer DIN 125 - A 3.2
12	8		DIN 912 M3 x 6
13	8		Washer DIN 125 - A 5.3
14	1		Motor Mount Socket
15	1		GT3 2mm 20T
16	8		635-2rsr
17	1		Endstop Bump Sample
18	13		DIN 912 M5 x 6
19	2		DIN 912 M5 x 55
20	2		DIN 912 M5 x 50
21	6		Stator Center Spacer Lo
22	7		DIN 912 M5 x 10
23	1		XRS-A Main Body
24	4		PRT-01-60
25	1		Detector Platform
26	1		Detector Driven Gear 250T
27	1		Motor Mount Detector Dr
28	1		GT3 2mm 80T
29	1		Endstop Bump Detector
30	4		Detector Spacer
31	4		DIN 912 M3 x 25
32	1		Stator Base
33	1		TUB00154-SA-W06
34	1		Tube Mount
35	1		Source Stand Socket
36	1		Tube Mount Extrusion
37	1		4020 90deg Bracket
38	1		Tube Mount Extrusion
39	4		DIN 912 M5 x 12
40	1		Sample Belt^X-MAGIX
41	1		Detector Belt^X-MAGIX
42	2		DIN 912 M5 x 30

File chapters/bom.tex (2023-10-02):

\begin{table}[!ht]
    \centering
    \caption[Mechanical parts full bill of materials]{Mechanical parts full bill of materials.}
    \label{tab:mech bom}
    \begin{tabular}{@{}rrllll@{}}
        \toprule
        ID&	Qty.&	Unit&	Name&	Standard&	Note\\
        \midrule
        1&	1&	&	Sample Platform                         &	&	FDM printed\\
        2&	1&	&	Sample Driven Gear 80T                  &		&	FDM printed\\
        3&	2&	&	W 61708                                 &	&	    \\
        4&	1&	&	Stator Center                           &	&		FDM printed\\
        5&	1&	&	Stator Center Spacer                    &	&		FDM printed\\
        6&	1&	&	Motor Mount Sample Drive                &	&		FDM printed\\
        7&	2&	&	17HM19-2004S                            &	&		\\
        8&	2&	&	Belt Tightener                          &	&		FDM printed\\
        9&	32&	&	M5 Hex Nut                              &	DIN 934&		\\
        10&	44&	&	M5 x 25                                 &	DIN 912&		\\
        11&	8&	&	Washer - A 3.2                          &	DIN 125&		\\
        12&	11&	&	M3 x 6                                  &	DIN 912&		\\
        13&	8&	&	Washer - A 5.3                          &	DIN 125&		\\
        14&	1&	&	Motor Mount Socket                      &	&		FDM printed\\
        15&	1&	&	GT3 2mm 20T                             &	&		\\
        16&	8&	&	635-2RS                                 &	&		\\
        17&	1&	&	Endstop Bump Sample                     &	&		FDM printed\\
        18&	17&	&	M5 x 6                                  &	DIN 912&		\\
        19&	2&	&	M5 x 55                                 &	DIN 912&		\\
        20&	2&	&	M5 x 50                                 &	DIN 912&		\\
        21&	6&	&	Stator Center Spacer Lock               &	&		FDM printed\\
        22&	7&	&	M5 x 10                                 &	DIN 912&		\\
        23&	1&	&	XRS-A                                   &	&		\\
        28&	1&	&	Detector Platform                       &	&		FDM printed\\
        29&	1&	&	Detector Driven Gear 250T               &	&		FDM printed\\
        30&	1&	&	Motor Mount Detector Drive              &	&		FDM printed\\
        31&	1&	&	GT3 2mm 80T                             &	&		\\
        32&	1&	&	Endstop Bump Detector                   &	&		FDM printed\\
        33&	4&	&	Detector Spacer                         &	&		FDM printed\\
        34&	4&	&	M3 x 25                                 &	DIN 912&		\\
        35&	1&	&	Stator Base                             &	&		FDM printed\\
        36&	1&	&	TUB00154-SA-W06                         &	&		\\
        37&	1&	&	Tube Mount                              &	&		FDM printed\\
        38&	1&	&	Source Stand Socket                     &	&		FDM printed\\
        39&	1&	&	Tube Mount Extrusion                    &	&		\\
        41&	1&	&	Tube Mount Extrusion                    &	&		\\
        42&	4&	&	M5 x 12                                 &	DIN 912&		\\
        43&	1&	&	Sample Belt                             &	&		\qty{6}{\milli\meter} 342T\\
        44&	1&	&	Detector Belt                           &	&		\qty{9}{\milli\meter} 600T\\
        45&	2&	&	M5 x 30                                 &	DIN 912&		\\
        46&	4&	&	PRT-01-60                               &	&		\\
        47&	10&	&	T-Slot Nut M5                           &	&		\\
        48&	2&	&	2020 90deg bracket                      &	        &		\\
        59& 1& \unit{\milli\metre}& Aluminum Slap 8x505x770 & & Material type non-critical\\
        % 58&&&&&&\\
        % 58&&&&&&\\
        \bottomrule
    \end{tabular}
\end{table}
\newpage
\begin{table}[!ht]
    \centering
    \caption[Electronic parts full bill of materials]{Electronic parts full bill of materials.}%
    \label{tab:electronic bom}
    \begin{tabular}{@{}rrllll@{}}
        \toprule
        ID&	Qty.&	Unit&	Name&	Description&	Note\\
        \midrule
        49& 2& & TMC2209&&\\
        50& 1& & BTT Octopus&&\\
        51& 1& & \qty{5}{\volt} PSU& RS-25-5&\\
        52& 1& & \qty{24}{\volt} PSU& LRS-150-24&\\
        53& 1& & ADC& MCP3202&\\
        54& 1& & DAC& TLV5618A&\\
        55& 1& & \qty{5}{\volt} reference& LM4040-Z&\\
        56& 1& & \qty{2.5}{\volt} reference& LT1009&\\
        57& 1& & Filtered Power Inlet& FN 284-6-06&\\
        58& 1& & Raspberry Pi 4 B&&\\
        \bottomrule
    \end{tabular}
\end{table}

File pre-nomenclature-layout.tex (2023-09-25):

\usepackage{longtable}
\usepackage[intoc]{nomencl}\makenomenclature
\renewcommand{\nomgroup}[1]{%
    \ifstrequal{#1}{A}{\item[\textbf{Abbreviations}]}{%
        \ifstrequal{#1}{G}{\vspace{20pt}\item[\textbf{Greek Symbols}]}{%
            \ifstrequal{#1}{L}{\vspace{20pt}\item[\textbf{Roman Symbols}]}{%
                \ifstrequal{#1}{S}{\vspace{20pt}\item[\textbf{Other Symbols}]}{%
                }%
            }%
        }%
    }%
}%
\renewcommand{\nomname}{Nomenclature}
\newcommand{\nomunit}[1]{%
\renewcommand{\nomentryend}{\hspace*{\fill}\(\left[\unit{#1}\right]\)}}
\setlength{\nomitemsep}{.3\parsep}

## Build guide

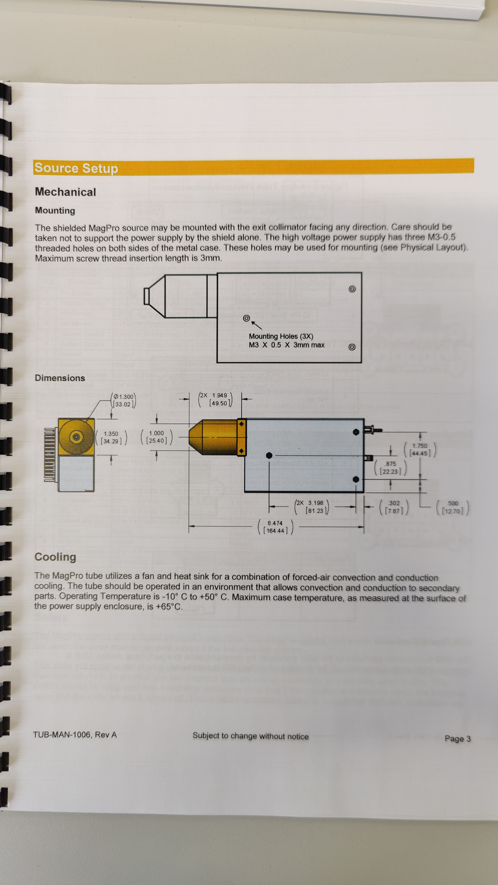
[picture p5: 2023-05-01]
docs/OnPaper/MANUAL_TUB-MAN-1007/2023-04-17-14-57-07-173.jpg

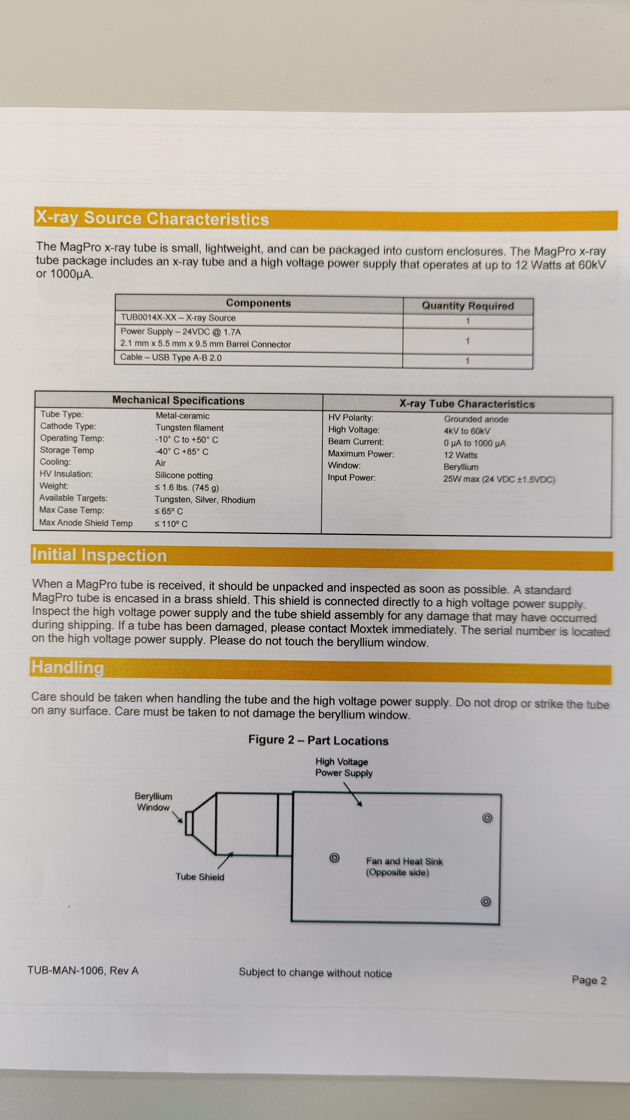
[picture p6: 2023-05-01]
docs/OnPaper/MANUAL_TUB-MAN-1007/2023-04-17-14-57-03-905.jpg

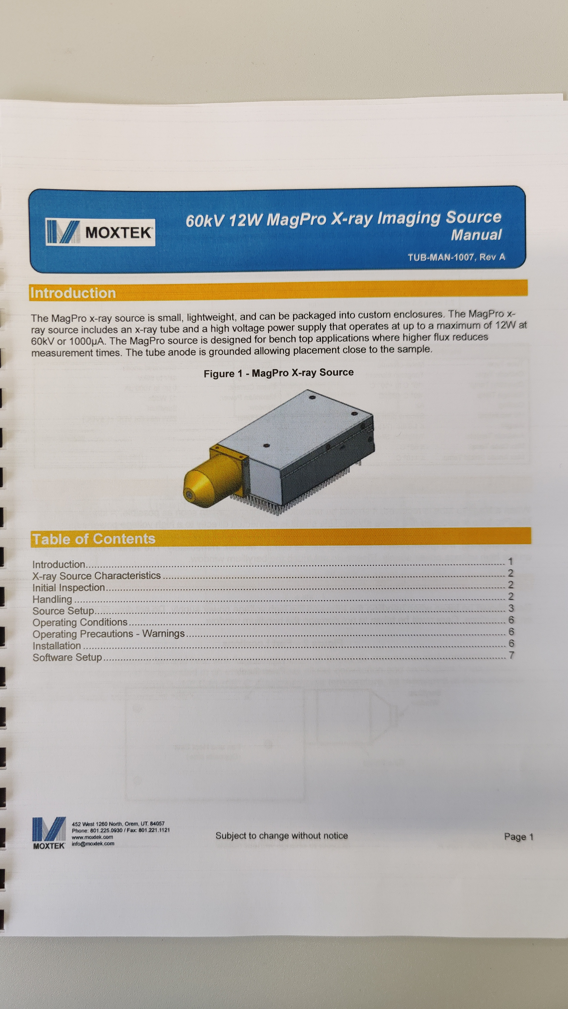
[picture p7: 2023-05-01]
docs/OnPaper/MANUAL_TUB-MAN-1007/2023-04-17-14-56-58-057.jpg

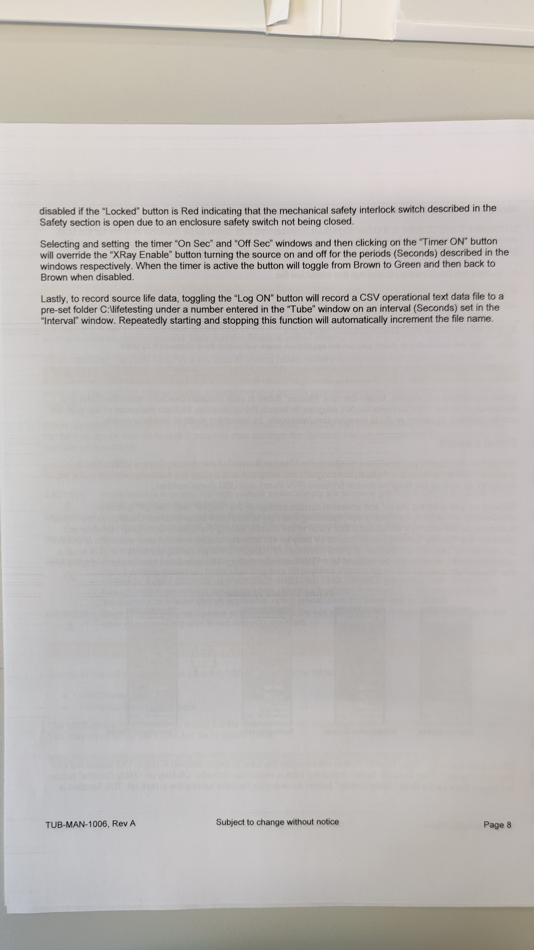
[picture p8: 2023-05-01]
docs/OnPaper/MANUAL_TUB-MAN-1007/2023-04-17-14-57-39-843.jpg

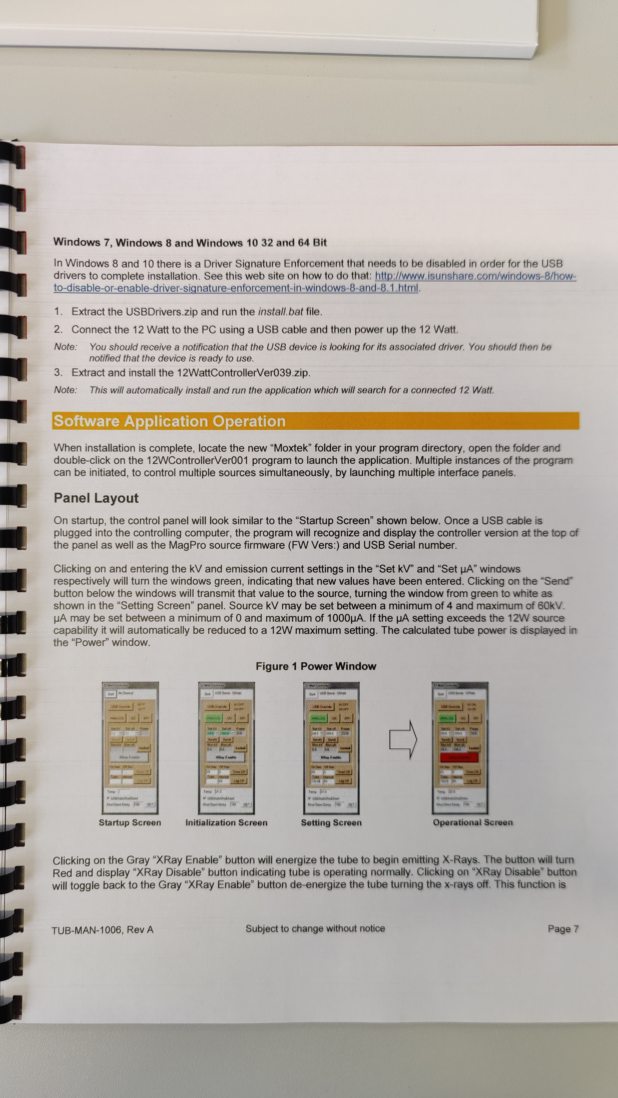
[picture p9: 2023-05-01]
docs/OnPaper/MANUAL_TUB-MAN-1007/2023-04-17-14-57-24-821.jpg

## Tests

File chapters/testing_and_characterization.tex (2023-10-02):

\chapter{Testing and Characterization}\label{chap:testing}
    \section{Data Acquisition}\label{sec:Data Acquisition}
        After some initial calibration,  three spectra were taken from brass, steel and lead.
        Each acquisition run was performed using \texttt{XMagix}'s \texttt{fixedRealtimeRun()} method set to \qty{30}{\second} and \texttt{clearMca} set to \texttt{false}.
        \Cref{tab:default detection parameters} below shows the acquisition values set during each run\footnote{A detailed description of each individual parameter can be found in the~\cite{Software.HandelRelease.2023,Manual.HandelAPIManual.Xiang,Manual.HandelProgrammersGuideMicroDXP.Xiang}.}.

        \begin{table}[!h]
            \centering
            \caption[Detector settings]{Detector settings taken from the technical specifications report coming with the detector. If not stated otherwise, the value stored on the device was used.}%
            \label{tab:default detection parameters}
            \begin{tabular}{@{}lS@{}}
                \toprule
                Parameter&      {Value}\\
                \midrule
                \texttt{parset}&     2.4\\
                \texttt{genset}&     0.0\\
                \texttt{fippi}&     0.0\\
                \texttt{clock\_speed}&     40.0\\
                \texttt{energy\_gap\_time}&     0.3\\
                \texttt{trigger\_peak\_time}&     0.05\\
                \texttt{trigger\_gap\_time}&     0.0\\
                \texttt{baseline\_length}&     512.0\\
                \texttt{trigger\_threshold}&     150.0\\
                \texttt{baseline\_threshold}&     120.0\\
                \texttt{energy\_threshold}&     0.0\\
                \texttt{peak\_interval\_offset}&     0.5\\
                \texttt{peak\_sample\_offset}&     0.0\\
                \texttt{max\_width}&     0.4\\
                \texttt{peak\_mode}&     0.0\\
                \texttt{peak\_interval}&     0.5\\
                \texttt{peak\_sample}&     0.0\\
                \texttt{polarity}&     1.0\\
                \texttt{preamp\_value}&     1.0\\
                \texttt{gain}&     4.484848\\
                \texttt{gain\_trim}&     1.05\\
                \texttt{number\_mca\_channels}&     8192.0\\
                \texttt{mca\_bin\_width}&     1.0\\
                \texttt{bytes\_per\_bin}&     3.0\\
                \texttt{adc\_trace\_wait}&     0.025\\
                \texttt{auto\_adjust\_offset}&     1.0\\
                \texttt{number\_of\_scas}&     0.0\\
                \bottomrule
            \end{tabular}
        \end{table}

        The parameter \texttt{gain} is set according to \cref{eq:gain calc}\cite{Manual.HandelAPIManual.Xiang}

        \begin{align}
            gain = \frac{1184}{DynRange \cdot PreampValue}
            \label{eq:gain calc}
        \end{align}

        with \(DynRange = \qty{40}{\kV}\) and \(PreampValue = \qty{6.6}{\milli\volt\per\kV}\).
        The latter is taken from the technical specification report where it is referred to as ``analog signal - gain''.
        \texttt{gain\_trim} was adjusted until the K-lines from the brass sample (copper and zinc) aligned with their respective peaks.
        Hereafter, the calibration was checked against a steel sample which is expected to expose itself as two peaks at irons \(K_{\alpha}\) and \(K_{\beta}\) lines and a lead sample.
        Within the energy range, lead should exhibit peaks at its \(L_{\alpha}\) and \(L_{\beta}\) lines.

        \begin{figure}[h]
            \centering
            \includesvg[width=\textwidth]{spectra/spectra_brass_steel_lead}
            \caption[Spectra taken from brass, lead and steel]{Spectra taken from brass, lead and steel at \qty{40}{\kV} using the acquisition values specified in \cref{tab:default detection parameters}.}%
            \label{fig:spectra 40kV}
        \end{figure}

        \Cref{fig:spectra 40kV} shows a combined plot of the spectra taken from brass, steel and lead at an acceleration voltage of \qty{40}{\kV} and a relatively low filament current of \qty{10}{\uA}.
        The full spectrum as read from the MCA is shown at the top and a detailed view of the highlighted region from \qtyrange{5}{20}{\kV} is shown below.
        With a rough calibration made, almost all peaks align good with the emission lines expected from the sample materials.
        % The \textit{microDXP} allows hardware based calibration and storage of value sets in its non-volatile memory as \texttt{parset}s and \texttt{globset}s.
        The spectra being in good agreement with the literature, the setup around the detector is considered functional.\par\medskip
        
        All characteristic energies used are taken from the online dataset provided by the \textsc{National Institute of Standards and Technology}\cite{Dataset.XRayTransitionEnergies.2005}.

    \section{Angular Resolution}\label{sec:angular resolution}
        The theoretical angular resolution for each individual stage is expressed in units of \unit{\degree\per\step} due to the incremental nature of the motion system.
        In general, it can be written as \cref{eq:angular resolution}:

        \begin{align}
            res_{\angle} &= \frac{360}{microsteps \cdot fullStepsPerRevolution} \cdot gearRatio
            \label{eq:angular resolution}
        \end{align}

        For the detector stage this 

        \begin{align}
            res_{\varphi} = \frac{\qty{360}{\degree}}{32 \cdot \qty{200}{\step}} \cdot \frac{80}{250} = \qty{0.018}{\degree\per\step}
        \end{align}

        for the detector stage and

        \begin{align}
            res_{\theta} = \frac{\qty{360}{\degree}}{32 \cdot \cdot \qty{200}{\step}} \cdot \frac{20}{80} \approx \qty{0.0141}{\degree\per\step}
        \end{align}

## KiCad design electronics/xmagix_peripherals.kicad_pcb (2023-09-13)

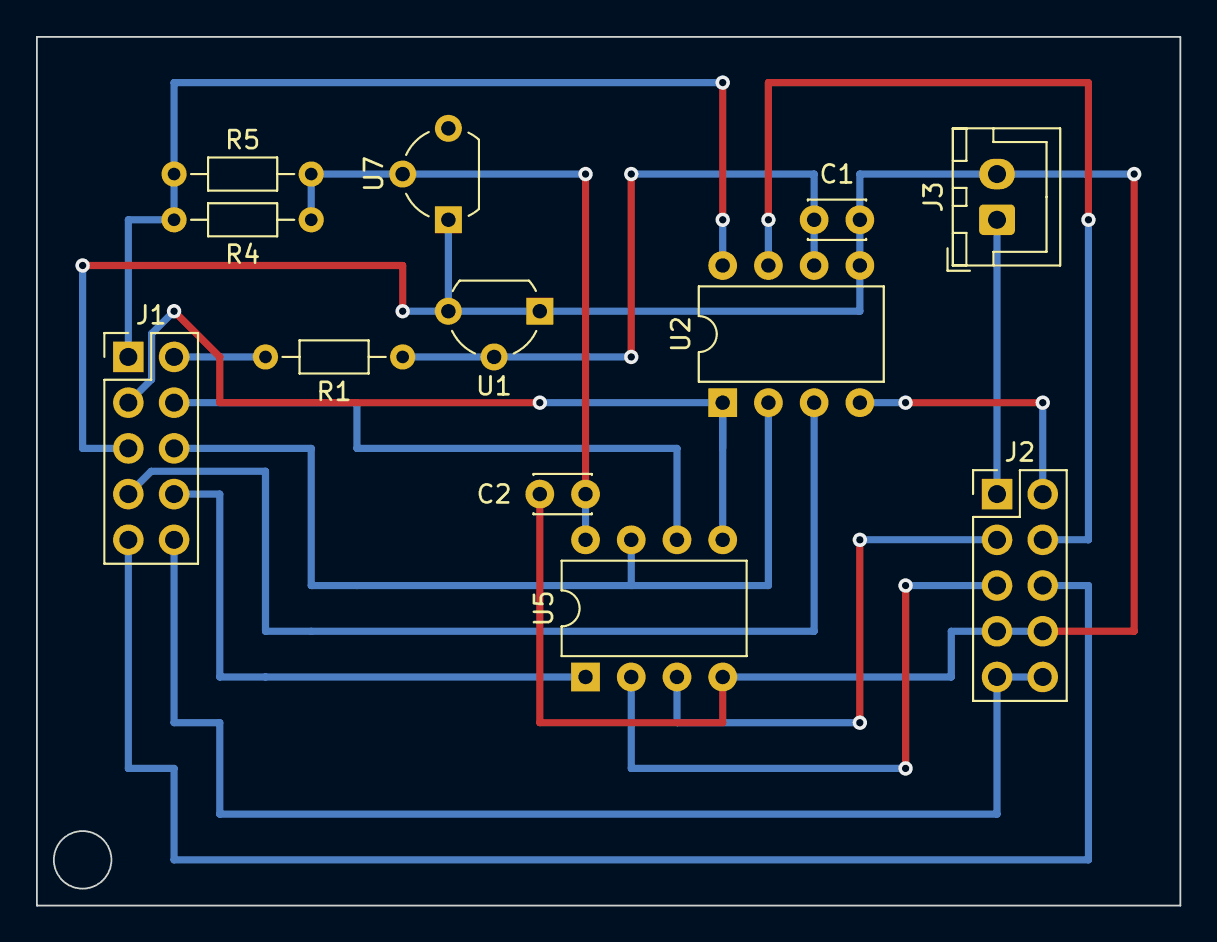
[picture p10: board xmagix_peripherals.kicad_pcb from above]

Board: 2 copper layers, 63.5 x 48.3 mm, 12 parts (0 on the bottom side), 17 nets.

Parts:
C1, C2: 1nF; C_Disc_D3.0mm_W2.0mm_P2.54mm
J1, J2: Conn_02x05_Counter_Clockwise; PinHeader_2x05_P2.54mm_Vertical
J3: Conn_01x02; JST_XH_B2B-XH-A_1x02_P2.54mm_Vertical
R1: 470R; R_Axial_DIN0204_L3.6mm_D1.6mm_P7.62mm_Horizontal
R4, R5: 12R; R_Axial_DIN0204_L3.6mm_D1.6mm_P7.62mm_Horizontal
U1: LT1009CZ; TO-92L_Wide
U2: TLV5618A; DIP-8_W7.62mm
U5: MCP3202; DIP-8_W7.62mm
U7: LM4040LP-5; TO-92L_Wide

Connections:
+2V5A: C1.2, R1.1, U1.2 (K), U2.6 (REF)
+3.3V: J1.2, R1.2
+5V: J1.1, R4.2, R5.2, U2.8 (VDD)
+5VA: C2.1, R4.1, R5.1, U5.8 (VDD/VREF), U7.2 (K)
+24V: J2.1, J3.1
CLK: J1.6, U2.2 (SCLK), U5.7 (CLK)
Current Control: J2.4, U2.7 (OUTB)
Current Monitor: J2.3, U5.3 (CH1)
Filament Enable: J1.10, J2.9, J2.10
Filament Ready: J1.9, J2.6
GND: C1.1, C2.2, J1.5, J2.7, J2.8, J3.2, U1.1 (A), U1.3 (Adj), U2.5 (AGND), U5.4 (VSS), U7.3 (A)
HV Control: J2.2, U2.4 (OUTA)
HV Monitor: J2.5, U5.2 (CH0)
MISO: J1.4, U5.6 (DOUT)
MOSI: J1.3, U2.1 (DIN), U5.5 (DIN)
~CS0: J1.8, U5.1 (~CS/SHDN)
~CS1: J1.7, U2.3 (~CS)

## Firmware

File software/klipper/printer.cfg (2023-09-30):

[include fluidd.cfg]

[virtual_sdcard]
path: /home/xmagix/printer_data/gcodes
on_error_gcode: CANCEL_PRINT

[mcu]
serial: /dev/serial/by-id/usb-Klipper_stm32f446xx_440022001251303431333234-if00

[printer]
kinematics: cartesian
max_velocity: 20
max_accel: 100
square_corner_velocity: 2.0

[stepper_x]
step_pin: PF13
dir_pin: PF12
enable_pin: !PF14
microsteps: 32
rotation_distance: 500 # unit mm
gear_ratio: 250:80
full_steps_per_rotation: 200
endstop_pin: ^PG6
position_endstop: 0 # unit mm
position_max: 300
homing_speed: 10 # unit mm/min
homing_retract_dist: 5 # unit mm
homing_positive_dir: false

[tmc2209 stepper_x]
uart_pin: PC4
interpolate: False
run_current: 0.8 # unit A
sense_resistor: 0.110 # unit Ohm
stealthchop_threshold: 0 # unit mm/min

[stepper_y]
step_pin: PG0
dir_pin: PG1
enable_pin: !PF15
microsteps: 32
rotation_distance: 160
gear_ratio: 80:20
endstop_pin: ^PG9
position_endstop: 0
position_max: 200
homing_speed: 10  #Max 100
homing_retract_dist: 5
homing_positive_dir: false

[tmc2209 stepper_y]
uart_pin: PD11
interpolate: True
run_current: 0.8
sense_resistor: 0.110
stealthchop_threshold: 0

[stepper_z]
step_pin: PF11
dir_pin: PG3
enable_pin: !PG5
microsteps: 16
rotation_distance: 8
endstop_pin: ^PD3
position_endstop: 0.5
position_max: 200

[homing_override]
gcode:
    SET_KINEMATIC_POSITION Z=0
axes: z

[force_move]
enable_force_move: true

[idle_timeout]
gcode:
timeout: 9999

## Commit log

2023-07-19 rotary stage first draft
2023-09-06 Schematics and Datasheets
    [raspberry.kicad_pcb, raspberry.kicad_sch]
2023-09-06 omg this setting is a blessing 🤩
2023-09-13 Tube Interface Board Docs
    [raspberry.kicad_pcb, raspberry.kicad_sch]
2023-09-23 endstops optical to tactile
    [raspberry.kicad_sch]
2023-09-25 interface board section
2023-09-25 schematics bug fix, gitignore
    [raspberry.kicad_sch]
2023-09-26 schematics renamed, raspi4b gpio sch added
    [raspberry4b.kicad_sch, xmagix_peripherals.kicad_pcb, xmagix_peripherals.kicad_sch]
2023-09-29 <Tube> roughly done
2023-09-30 section kinematics
    [raspberry4b.kicad_sch, xmagix_peripherals.kicad_sch]
